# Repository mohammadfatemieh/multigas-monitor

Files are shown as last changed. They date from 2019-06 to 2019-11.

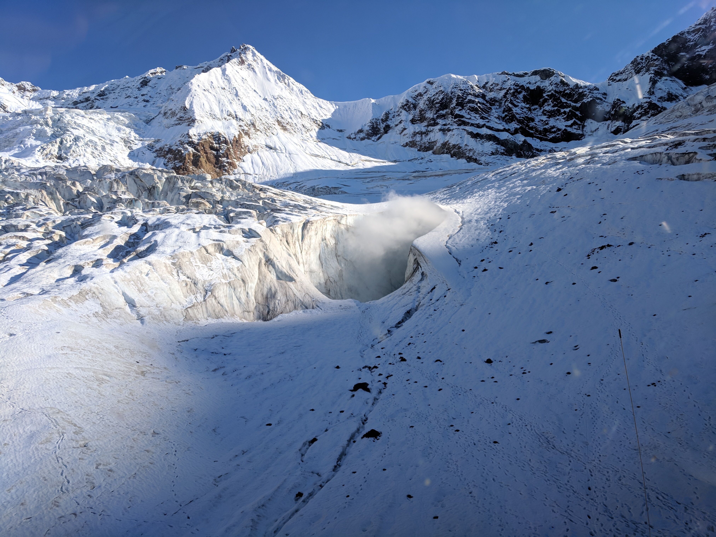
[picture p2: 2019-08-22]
Documents/FUMAROLE.jpeg

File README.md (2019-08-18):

# VAMoS MultiGas Monitor
Research instrument for monitoring gaseous concentrations.

## Overview
The VAMoS MultiGas Monitor is an improvement to the exisiting MGM used by SFU Volcanology. The current MGM cannot be used for more than
1-2 hours and must be manually controlled by an on-site researcher. VAMoS is a device that can be deployed for multi-week remote
monitoring in the glacial environment on Mt. Meager's Job Glacier.

## Features
* Onboard microprocessing using the ESP32WROOM-32U micrcontroller
* Inverted-F trace antenna for WiFi transmission at 2.4GHz
* 4-20mA signal processing for state-of-the-art Alphasense electrochemical and NDIR gas sensors
* Onboard BME280 temperature, humidity, and pressure sensor; XA1100 GPS module
* Connector for external DS18B20 temperature probe
* microSD card connector for data storage
* LED indicators to show system health and operation status

## Known Issues
* See document

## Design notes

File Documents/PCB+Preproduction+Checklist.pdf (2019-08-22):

# PCB Preproduction Checklist

ID | Item | Check

0.0 Schematic

0.1 | Boot strapping note added to MCU sheet? Triple-check default states due to internal vs. external pull-up/pull-down resistors.
0.2 | Boot strapping pins accessible via TPs?
0.3 | Debug pins broken out to SMD header?
0.4 | Test points on all unused pins?
0.5 | Small ceramic bypass cap on enable/reset lines?
0.6 | Noise-sensitive analog systems have separate power rail from low-noise LDO? Inside a grounded RF shield?
0.7 | All peripherals have TVS diodes as gatekeeper?
0.8 | All (UART, SPI, etc.) signals have 0R series resistors to make placeholder for ferrite bead?
0.9 | Check default internal state of IO pins (pull-up vs. pull-down) and add external resistors where necessary. Option to add both and DNP where necessary.

1.0 Footprints

1.1 | All components have 3D extrusion?
1.2 | Footprints double-checked?
1.3 | Footprints triple-checked?
1.4 | Detailed 3D CAD populated for all ICs, especially connectors? Check manufacturer website if not available through distributor.
1.4 | Connectors facing outwards?
1.5 | Pin 1 indicator present on silkscreen of all ICs? Polarity (e.g. diodes, LEDs, electrolytic caps) indicated?

2.0 Power Plane

2.1 | Islands for separate rails?

2.2 Island bridges ~20 mil width (check with trace width calculator)

3.0 Ground Plane

3.1 | Stitching vias?
3.2 | Direct connect polygons for GND vias?
3.3 | No net antennae on DRC? Add vias to planes that extend into stubs without enough stitching vias.

4.0 Vias

4.1 | Tented on top and bottom (except for thermal relief GND vias underneath large ICs)?
4.2 | 10-20mil ratio?

5.0 Miscellaneous

5.1 | Mounting holes in each corner, M3 (3mm dia) screws
5.2 | Board outline defined on Keep-Out or Mechanical 1 layer with curved edges
5.3 | Board outlines clearance set to 20-40mil
5.4 | Useful TP and connector labels on silkscreen? Specify polarity of power inputs, DC vs. AC, boot strapping TPs, status LEDs, power rails, and ground TPs.
5.5 | Light passives (e.g. 0402, 0603 or less) have even amount of copper pours on either side to ensure equal melt distribution?

6.0 Manufacturability

6.1 | Min. 3 fiducials per side to ensure manufacturing alignment?
6.2 | No acid traps (acute angle traces?)
6.3 | Latest PCB design rules (.RUL) imported as per manufacturer's specifications?
6.4 | Board thickness/stack-up is 1.6mm / 63mil (for four-layer) PCB?

7.0 RF

7.1 | Antenna trace length impedance matched?
7.2 | Ground vias around perimeter?
7.3 | External/shielding pins of connector (if applicable) grounded?

8.0 Power Supply

8.1 | Bypass caps close to IC, in order of lowest capacitance to highest?
8.2 | High-frequency traces thick (min. pad thickness, if possible use a plane)

8.3 | No traces underneath switching inductor?
8.4 | Via ampacity: 18-35mil in/out diameter via on power traces? Multiple for connecting large planes (use min. 3 vias or make larger). Check with trace width calculator, specifically for internal layers.

9.0 Bill of Materials (BOM)

9.1 | Only CT (Cut Tape) PNs used? (Digi-Reel costs extra $8-10)
9.2 | Checked twice?
9.3 | Checked thrice?

10.0 Post Production

10.1 | Export 3D STEP model of PCB for enclosure design team
10.2 | Zip release files and label with board house and order date
10.3 | Upload all project files to GitHub
10.4 | Order BOM. If sufficient amount of parts are cheaper through Mouser, Future, etc. and cart is large enough to get free shipping on all orders, then order through multiple distributors. Otherwise, order through DigiKey.

FINAL CHECK:

Is the PCB looking SEX? | HELL YEAH | NAH

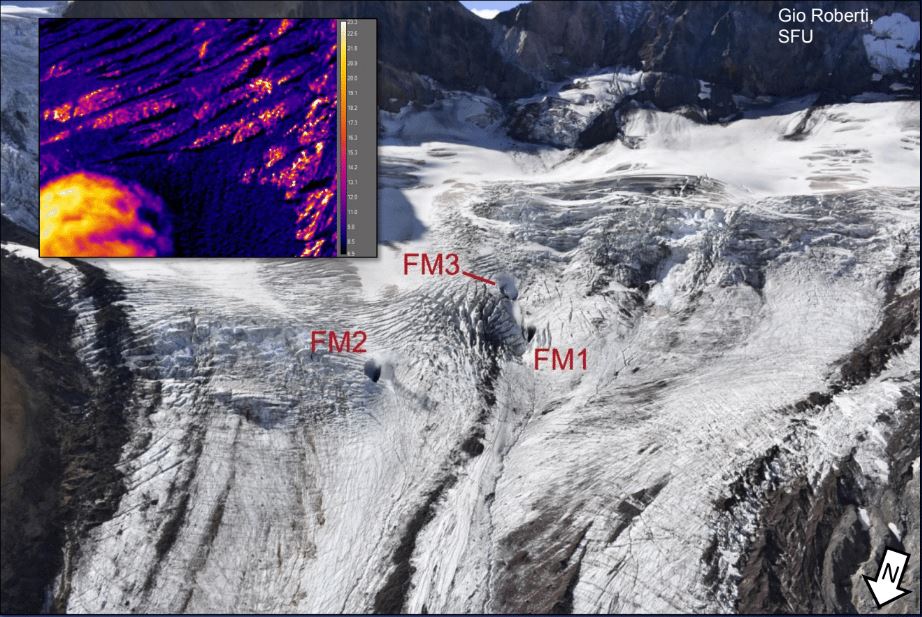
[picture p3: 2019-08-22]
Documents/fumaroles.JPG

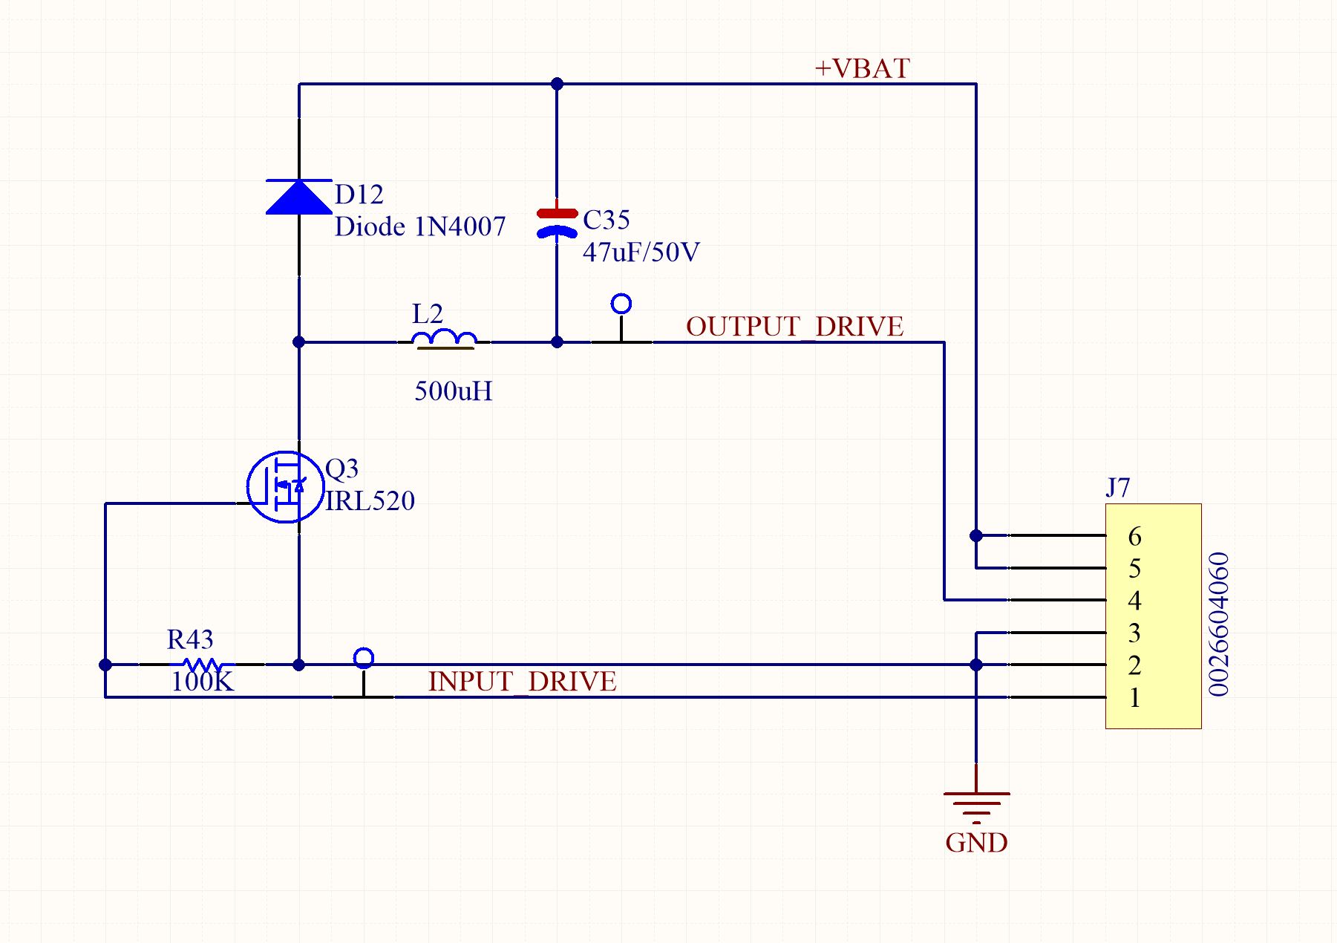
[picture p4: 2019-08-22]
Documents/pumpdrive.JPG

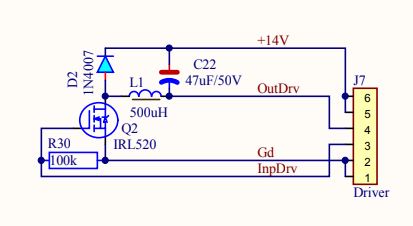
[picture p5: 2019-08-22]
Documents/Pump Driver.JPG

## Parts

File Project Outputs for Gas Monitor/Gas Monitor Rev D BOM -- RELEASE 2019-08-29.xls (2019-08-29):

Description | Designator | Footprint | Quantity | Manufacturer | Manufacturer Part Number | Supplier 1 | Supplier Part Number 1 | Value | VAMoS Rev D
Push Button Top | B200, B201 | PTS 815 | 2 | C&K Components | PTS815 SJG 250 SMTR LFS | Digi-Key | CKN12217-1-ND |  | BOM
 | C100, C101, C102, C103, C104, C105, C106, C107, C108, C109, C110, C111, C112, C113, C114, C115, C116, C117, C200, C202, C204, C205, C206, C208, C209, C306, C311, C318, C405, C406, C407, C501, C502, C503, C605, C608 | CAPC1005X06N | 36 | Samsung | CL05A104KA5NNNC | Digi-Key | 1276-1043-1-ND | 100nF | 2019-08-29
Capacitor | C201 | CAPC1005X06N | 1 | Samsung | CL05A106MP8NUB8 | Digi-Key | 1276-6830-1-ND | 10u
Cap,4.7uF,10V,20%,X5R,0402, Cap,4.7uF,16V,20%,X5R,0402 | C203, C207, C300, C302, C305, C307, C312, C313, C314, C317 | C1005[0402] | 10 | Samsung Electro-Mechanics | CL05A475MO5NUNC | Digi-Key | 1276-6836-1-ND | 4u7
 | C303, C304, C315, C321, C322, C603, C609, C610, C611 | CAPC2012X14N | 9 | Murata | GRM21BR61E226ME44K | Digi-Key | 490-14661-1-ND | 22u
 | C308, C319 | CAPC1005X06N | 2 | Samsung | CL05B153KO5NNNC | Digi-Key | 1276-1524-1-ND | 15n
Cap,3.3nF,50V,10%,X7R,0603 | C309 | C1608[0603] | 1 | Samsung | CL10B332KB8NNNC | Digi-Key | 1276-1758-1-ND | 3n3
 | C310, R227 | CAPC1005X06N, RESC1005X03N | 2 | N/A | N/A | N/A | N/A | DNP
 | C316, C320 | C3225[1210]_Tall | 2 | Murata | GRM32ER61A107ME20L | Digi-Key | 490-9969-1-ND | 100u
CAP 4.7uF 10V ±10% X5R 0603 | C400, C401, C402, C403, C404 | CAPC1005X06N | 5 | Samsung | CL05A105MP5NNNC | Digi-Key | 1276-1448-1-ND | 1u
CAP ALUM 47UF 20% 50V SMD | C500 | Panasonic S-V D8 | 1 | Panasonic | EEE-1HA470XAP | Digi-Key | PCE4622CT-ND
CAP 1µF 25V ±10% X7R 0603 | C600, C601, C602, C604, C606, C607 | C1608[0603] small | 6 | Samsung | CL10B105KA8NNNC | Digi-Key | 1276-1184-1-ND | 1u
5V TVS | D100, D101, D102, D103, D104, D105, D106, D107, D200, D209 | NXP PTVSxS1UR-Series (SOD123W) | 10 | Nexperia | PTVS5V0S1UR,115 | Digi-Key | 1727-5229-1-ND
TVS Diode | D201, D202, D203, D205, D206 | SODFL100X40-2N | 5 | ON Semiconductor | ESD7951ST5G | Digi-Key | ESD7951ST5GOSCT-ND
LED RGB Clear 624nm/526nm/469nm 2V/3.1V/3V PLCC-6 | D208 | VLMRGB6112 | 1 | Vishay Semiconductor Opto Division | VLMRGB6112-00-GS08 | Digi-Key | VLMRGB6112-00-GS08CT-ND
12V TVS | D300, D501, D502, D600, D601, D602 | NXP PTVSxS1UR-Series (SOD123W) | 6 | Nexperia | PTVS12VS1UR,115 | Digi-Key | 1727-5325-1-ND
LED Blue Diffused 0603 | D301 | LED_0603 | 1 | Rohm | SMLE12BC7TT86 | Digi-Key | 511-1589-1-ND
LED Green Diffused 0603 | D302, D303, D304, D305, D407, D606 | LED_0603 | 6 | Rohm | SML-D12M8WT86 | Digi-Key | 511-1578-1-ND
Diode Standard 600V 2A Surface Mount SMA | D306, D500, D603, D604, D605 | Diode SMA DIOM5226X240N | 5 | ON Semi | MURA260T3G | Digi-Key | MURA260T3GOSCT-ND
3.3V TVS | D400, D401, D402, D403, D404, D405 | NXP PTVSxS1UR-Series (SOD123W) | 6 | Nexperia | PTVS3V3S1UTR,115 | Digi-Key | 1727-1416-1-ND
300mA General Purpose | D406 | SOD-123FL_TVS | 1 | Diodes Incorporated | 1N4148W-7-F | Digi-Key | 1N4148W-FDICT-ND
120 Ohms @ 100MHz 1 Power Line Ferrite Bead 0603 (1608 Metric) 2.7A 35mOhm | FB500 | RESC1608X06N | 1 | Taiyo Yuden | BKP1608HS121-T | Digi-Key | 587-1923-1-ND
CONN HEADER VERT 2POS 2.54MM | J100, J101, J102, J103 | 22-23-2021 | 4 | Molex | 22-23-2021 | Digi-Key | WM4200-ND
Connector Header Through Hole 4 position 0.100" (2.54mm) | J104, J105, J106, J107, J401 | 22-23-2041 | 5 | Molex | 22232041 | Digi-Key | WM4202-ND
CONN HEADER VERT 2POS 2.54MM | J200 | HDR_1x2_0.100" | 1 | Sullins | PRPC002SAAN-RC | Digi-Key | S1011EC-02-ND
 | J201 | SD-47219-001 | 1 | Molex | 472192001 | Digi-Key | WM6698CT-ND
Connector Header Through Hole 3 position 0.100" (2.54mm) | J202, J400, J500 | 22-23-2031 | 3 | Molex | 22232031 | Digi-Key | WM4201-ND
 | J203 | UJ2-MIBH2-4-SMT | 1 | CUI | UJ2-MIBH2-4-SMT-TR | Digi-Key | 102-4007-1-ND
5.08mm Spring Cage, Tension Clamp, Pheonix Contact, 2pos, THD | J300, J600, J601, J602 | 5.08MM 2POS TERMBLOCK | 4 | Phoenix Contact | 1790283 | Digi-Key | 277-6722-ND
DigiKey # 36-2997-ND | J402 | 2997 11.6MM COIN CELL | 1 | Keystone Electronics | 2997 | Digi-Key | 36-2997-ND
CONUFL001-SMD-T | J403 | CONUFL001-SMD-T | 1 | Linx Technologies | CONUFL001-SMD-T | Digi-Key | CONUFL001-SMD-TCT-ND
Ferrite,SMD,3A,30Ohm,0805 | L300, L301, L400 | L2012[0805] | 3 | Bourns Inc. | MH2029-300Y | Digi-Key | MH2029-300YCT-ND
2 Line Common Mode Choke Surface Mount 60 Ohms @ 100MHz 15A DCR 0.75mOhm | L302, L600, L601, L602 | CM3421Y600R-10 | 4 | Laird | CM3421Y600R-10 | Digi-Key | 240-2501-1-ND
Fixed Inductor,SMD,33nH,550mA,132mOhmDCR,2.5GHz,0603 | L401 | L1608[0603] | 1 | Murata | LQW18AN33NJ10D | Digi-Key | 490-6885-1-ND | 33n
470µH Shielded Wirewound Inductor 1.4A 560mOhm Max Nonstandard | L500 | WE-PD 1210 | 1 | Wurth Electronics | 7447709471 | Digi-Key | 732-1699-1-ND | 470u
General Purpose Transistor, NPN Silicon, 3-Pin SOT-23, Tape and Reel | Q200, Q201 | ONSC-SOT-23-3-318-08_V | 2 | Comchip Technology | SS8050-G | Digi-Key | 641-1790-1-ND
MOSFET N-CH 100V 28A D2PAK | Q500 | D2PAK | 1 | Vishay Siliconix | IRL540SPBF | Digi-Key | IRL540SPBF-ND
RES 1K Ohm ±5%, 0.25W,1/4W 0603 | R100, R105, R106, R107, R112, R114, R116, R118, R215 | RESC1005X03N | 9 | Panasonic | ERJ-2RKF1001X | Digi-Key | P1.00KLCT-ND | 1k
Res,SMD,4R99,1/4W,5% | R101, R102, R103, R104, R113, R115, R117, R119 | RESC1005X03N | 8 | Stackpole | RMCF0402FT4R99 | Digi-Key | RMCF0402FT4R99CT-ND | 4R99
Res,SMD,22k,0603,5%,1/4W | R108, R109, R110, R111, R120, R121, R122, R123 | RESC1005X03N | 8 | Panasonic | ERJ-2RKF2202X | Digi-Key | P22.0KLDKR-ND | 22k
 | R200, R201, R202, R203, R204, R205, R206, R209, R210, R212, R221, R222, R223, R233 | RESC1005X03N | 14 | Panasonic | ERJ-2GE0R00X | Digi-Key | P0.0JCT-ND | 0R
Res,SMD,1/10W,3K16,0603,1% | R216 | RESC1005X03N | 1 | Stackpole Electronics | RMCF0603FT3K16 | Digi-Key | RMCF0603FT3K16CT-ND | 3k16
Res,SMD,4K53,1/10W,1%,0603 | R217 | RESC1005X03N | 1 | Yageo | RC0603FR-074K53L | Digi-Key | 311-4.53KHRCT-ND | 4k53
RES 10k Ohm, [NoValue], RES 1K Ohm ±5%, 0.25W,1/4W 0603 | R220, R228, R229, R230, R300, R304, R400, R404, R405, R406, R409 | RESC1005X03N | 11 | Panasonic | ERJ-2RKF1002X | Digi-Key | P10.0KLCT-ND | 10k
Res,SMD,22k,0603,5%,1/4W | R224 | R1005[0402] | 1 | Panasonic | ERJ-2RKF2212X | Digi-Key | P22.1KLCT-ND | 22k1
Res,SMD,22k,0603,5%,1/4W | R225 | R1005[0402] | 1 | Panasonic | ERJ-2RKF4752X | Digi-Key | P47.5KLCT-ND | 47k5
 | R226, R407, R408 | R1005[0402] | 3 | Panasonic | ERJ-2RKF2001X | Digi-Key | P2.00KLDKR-ND | 2k
 | R231 | RESC1005X03N | 1 | Panasonic | ERJ-2RKF6981X | Digi-Key | P6.98KLCT-ND | 6k98
 | R232 | RESC1005X03N | 1 | Panasonic | ERJ-2RKF2101X | Digi-Key | P2.10KLCT-ND | 2k1
Res,SMD,0603,1/10W,100K,1% | R301 | RESC1005X03N | 1 | Panasonic | ERJ-2RKF1003X | Digi-Key | P100KLCT-ND | 100k
RES 1K Ohm ±5%, 0.25W,1/4W 0603 | R302, R305, R602 | R1608[0603] small | 3 | Yageo | RC0603FR-071K2L | Digi-Key | 311-1.20KHRCT-ND
RES SMD 71.5K OHM 1% 1/10W 0603 | R303 | RESC1005X03N | 1 | Panasonic Electronic Components | ERJ-2RKF7152X | Digi-Key | P71.5KLCT-ND
RES 1K Ohm ±5%, 0.25W,1/4W 0603 | R306, R307 | R1608[0603] small | 2 | Rohm | RC0603FR-07560RL | Digi-Key | 311-560HRCT-ND
RES 1K Ohm ±5%, 0.25W,1/4W 0603 | R308, R401 | R1608[0603] small | 2 | Rohm | RC0603FR-07330RL | Digi-Key | 311-330HRCT-ND | 330R
RES 1K Ohm ±5%, 0.25W,1/4W 0603 | R402, R403 | RESC1005X03N | 2 | Panasonic | ERJ-2RKF4700X | Digi-Key | P470LCT-ND | 470R
 | R500 | RESC1608X06N | 1 | Panasonic | ERJ-3GEY0R00V | Digi-Key | P0.0GCT-ND | 0R
 | R501 | RESC1608X06N | 1 | Panasonic | ERJ-3GEYJ104V | Digi-Key | P100KGCT-ND | 100k
 | R600 | RESC1608X06N | 1 | Panasonic | ERA-3AEB5362V | Digi-Key | P53.6KDBCT-ND | 53k6
 | R601 | RESC1608X06N | 1 | Panasonic | ERA-3AEB6981V | Digi-Key | P6.98KDBCT-ND | 6k98
Quad opamplifiers | U100, U101 | SOIC-14 | 2 | Texas Instruments | LMH6644MAX/NOPB | Digi-Key | 296-35336-1-ND
Microcontroller WIFI Module 32Mbits SPI Flash | U200 | ESP32-WROOM-32U | 1 | Espressif Systems | ESP32-WROOM-32U | Digi-Key | 1904-1026-1-ND
USB to UART converter | U201 | QFN50P500X500X80_HS-29N | 1 | Silicon Labs | CP2102N-A01-GQFN28R | Digi-Key | 336-4738-1-ND
USB ESD Solution with Power Clamp, 4 Channels, -40 to +85 degC, 6-pin SON (DRY), Green (RoHS & no Sb/Br) | U202 | DRY0006A | 1 | Texas Instruments | TPD4S012DRYR | Digi-Key | 296-24244-1-ND
1A 3.3V LDO | U300 | SOT230P700X165-4N | 1 | Diodes Incorporated | ZLDO1117G50TA | Digi-Key | ZLDO1117G50DICT-ND
High Side Load Switch | U301 | SOT23 | 1 | Texas Instruments | TPS22810DBVR | Digi-Key | 296-45297-1-ND
DC-DC: 0.9-6V 2A output, 3-17V input. Non-isolated. | U302 | SIL0008D | 1 | Texas Instruments | TPS82140SILT | Digi-Key | 296-47089-1-ND
1A 3.3V LDO | U303 | SOT230P700X165-4N | 1 | Diodes Incorporated | ZLDO1117QG33TA | Digi-Key | ZLDO1117QG33TADICT-ND
GPS Module | U400 | XA1100 | 1 | Sierra Wireless | XA1100_1103872 | Digi-Key | 1645-1094-1-ND
SENSOR Humidity Temperature 0 ~ 100% RH I²C SPI ±3% 1s 8-Pin LGA | U401 | BME280 | 1 | Bosch | BME280 | Digi-Key | 828-1063-1-ND
Linear Voltage Regulator IC Positive Adjustable 1 Output 3A D2PAK-5 | U600 | D2PAK-5 | 1 | ON Semiconductor | NCP57302DSADJR4G | Digi-Key | NCP57302DSADJR4GOSCT-ND
Coin cell battery 11.6mm Silver Oxide |  |  | 2 | Energizer Battery Company | 357-303VZ | Digi-Key | N102-ND
Molex 22-23 2pin housing |  |  | 10 | Molex | 22-01-3027 | Digi-Key | WM2000-ND
Molex 22-23 3pin housing |  |  | 12 | Molex | 22-01-3037 | Digi-Key | WM2001-ND
Molex 22-23 4pin housing |  |  | 10 | Molex | 22013047 | Digi-Key | WM2002-ND
Molex KK crimp tool set |  |  | 1 | Molex | 76650-0009 | Digi-Key | WM9983-ND
TE AMP FASTON connector |  |  | 10 | TE Connectivity | 444334-3 | Digi-Key | A117966CT-ND
TE AMP FASTON sleeve |  |  | 10 | TE Connectivity | 170823-6 | Digi-Key | A106979-ND

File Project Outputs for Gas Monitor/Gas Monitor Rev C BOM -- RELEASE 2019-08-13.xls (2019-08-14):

Description | Designator | Footprint | Quantity | Supplier 1 | Supplier Part Number 1 | Manufacturer | Manufacturer Part Number
Push Button Top | B200, B201 | PTS 815 | 2 | Digi-Key | CKN12217-1-ND | C&K Components | PTS815 SJG 250 SMTR LFS
 | C100, C101, C102, C103, C104, C105, C106, C107, C200, C202, C204, C206, C208, C209, C306, C311, C318, C405, C406, C407, C408, C409 | CAPC1005X06N | 22 | Digi-Key | 1276-1043-1-ND | Samsung | CL05A104KA5NNNC
Capacitor | C201 | CAPC1005X06N | 1 | Digi-Key | 1276-6830-1-ND | Samsung | CL05A106MP8NUB8
Cap,4.7uF,10V,20%,X5R,0402, Cap,4.7uF,16V,20%,X5R,0402 | C203, C207, C300, C302, C305, C307, C312, C313, C314, C317 | C1005[0402] | 10 | Digi-Key | 1276-6836-1-ND | Samsung Electro-Mechanics | CL05A475MO5NUNC
CAP 1µF 25V ±10% X7R 0603 | C301 | C1608[0603] small | 1 | Digi-Key | 1276-1184-1-ND | Samsung | CL10B105KA8NNNC
22uF 50V Hybrid Polymer Capacitor | C303 | Radial Can F61 6.6x6.6 | 1 | Digikey | 565-4188-6-ND | United Chemi-Con | HHXB500ARA220MF61G
CAP 22µF 16V ±20% X5R 0805 | C304 | C2012[0805] | 1 | Digi-Key | 1276-6780-1-ND | Samsung Electro-Mechanics | CL21A226MOCLRNC
 | C308, C319 | CAPC1005X06N | 2 | Digi-Key | 1276-1524-1-ND | Samsung | CL05B153KO5NNNC
Cap,3.3nF,50V,10%,X7R,0603 | C309 | C1608[0603] | 1 | Digi-Key | 1276-1758-1-ND | Samsung | CL10B332KB8NNNC
 | C315 | Radial Can Size G | 1 | Digikey | P15442CT-ND | Panasonic | EEH-ZA1H101P
 | C316 | C3225[1210]_Tall | 1 | Digi-Key | 490-9969-1-ND | Murata | GRM32ER61A107ME20L
CAP 4.7uF 10V ±10% X5R 0603 | C400, C401, C402, C403, C404 | CAPC1005X06N | 5 | Digi-Key | 1276-1448-1-ND | Samsung | CL05A105MP5NNNC
5V TVS | D100, D101, D102, D103, D104, D105, D106, D107 | NXP PTVSxS1UR-Series (SOD123W) | 8 | Digi-Key | 1727-5229-1-ND | Nexperia | PTVS5V0S1UR,115
3.3V TVS | D200, D201, D400, D401, D402, D403, D404, D405, D409, D410 | NXP PTVSxS1UR-Series (SOD123W) | 10 | Digi-Key | 1727-1416-1-ND | Nexperia | PTVS3V3S1UTR,115
TVS Diode | D202, D203, D204, D205, D206, D207 | SODFL100X40-2N | 6 | Digi-Key | ESD7951ST5GOSCT-ND | ON Semiconductor | ESD7951ST5G
LED RGB Clear 624nm/526nm/469nm 2V/3.1V/3V PLCC-6 | D208 | VLMRGB6112 | 1 | Digi-Key | VLMRGB6112-00-GS08CT-ND | Vishay Semiconductor Opto Division | VLMRGB6112-00-GS08
12V TVS | D300 | NXP PTVSxS1UR-Series (SOD123W) | 1 | Digi-Key | 1727-5325-1-ND | Nexperia | PTVS12VS1UR,115
LED Green Diffused 0603 | D301, D302, D303, D304, D305, D407 | LED_0603 | 6 | Digi-Key | 511-1578-1-ND | Rohm | SML-D12M8WT86
300mA General Purpose | D406 | SOD-123FL_TVS | 1 | Digi-Key | 1N4148W-FDICT-ND | Diodes Incorporated | 1N4148W-7-F
Connector Phoenix 10 pin | J100 | 6410/10pin | 1 | Digi-Key | WM4308-ND | Molex | 22053101
Connector 2 pin | J200 | 6410/2pin | 1 | Digi-Key | WM19468-ND | Molex | 22232023
 | J201 | SD-47219-001 | 1 | Digi-Key | WM6698CT-ND | Molex | 472192001
 | J202 | 502584-0370 | 1 | Digi-Key | WM14461CT-ND | Molex | 5025840370
 | J203 | UJ2-MIBH2-4-SMT | 1 | Digi-Key | 102-4007-1-ND | CUI | UJ2-MIBH2-4-SMT-TR
5.08mm Spring Cage, Tension Clamp, Pheonix Contact, 2pos, THD | J300 | 5.08MM 2POS TERMBLOCK | 1 | Digi-Key | 277-6722-ND | Phoenix Contact | 1790283
3POS,THD,TENSION CLAMP,PHOENIX CONTACT | J400 | 3POS PHOENIX | 1 | Digi-Key | 277-1623-ND | Phoenix Contact | 1985205
 | J401 | 502584-0470 | 1 | Digi-Key | WM10615CT-ND | Molex | 502584-0470
DigiKey # 36-2997-ND | J402 | 2997 11.6MM COIN CELL | 1 | Digi-Key | 36-2997-ND | Keystone Electronics | 2997
CONUFL001-SMD-T | J403 | CONUFL001-SMD-T | 1 | Digi-Key | CONUFL001-SMD-TCT-ND | Linx Technologies | CONUFL001-SMD-T
0.100" Female Header | J404 | 0.100" 9PIN | 1 | Digi-Key | S7042-ND | Sullins | PPPC091LFBN-RC
Ferrite,SMD,3A,30Ohm,0805 | L300, L301, L400 | L2012[0805] | 3 | Digi-Key | MH2029-300YCT-ND | Bourns Inc. | MH2029-300Y
Fixed Inductor,SMD,33nH,550mA,132mOhmDCR,2.5GHz,0603 | L401 | L1608[0603] | 1 | Digi-Key | 490-6885-1-ND | Murata | LQW18AN33NJ10D
General Purpose Transistor, NPN Silicon, 3-Pin SOT-23, Tape and Reel | Q200, Q201 | ONSC-SOT-23-3-318-08_V | 2 | Digi-Key | 641-1790-1-ND | Comchip Technology | SS8050-G
RES 1K Ohm ±5%, 0.25W,1/4W 0603 | R100, R105, R106, R107, R112, R114, R116, R118 | RESC1005X03N | 8 | Digi-Key | P1.00KLCT-ND | Panasonic | ERJ-2RKF1001X
Res,SMD,4R99,1/4W,5% | R101, R102, R103, R104, R113, R115, R117, R119 | RESC1005X03N | 8 | Digi-Key | RMCF0402FT4R99CT-ND | Stackpole | RMCF0402FT4R99
Res,SMD,22k,0603,5%,1/4W | R108, R109, R110, R111, R120, R121, R122, R123 | RESC1005X03N | 8 | Digi-Key | P22.0KLDKR-ND | Panasonic | ERJ-2RKF2202X
 | R200, R201, R202, R203, R204, R205, R206, R207, R208, R209, R210, R211, R221, R222, R223 | RESC1005X03N | 15 | Digi-Key | P0.0JCT-ND | Panasonic | ERJ-2GE0R00X
RES 1K Ohm ±5%, 0.25W,1/4W 0603 | R215 | R1608[0603] small | 1 | Digi-Key | RHM1.0KDCT-ND | Rohm | ESR03EZPJ102
Res,SMD,1/10W,3K16,0603,1% | R216 | R1608[0603] small | 1 | Digi-Key | RMCF0603FT3K16CT-ND | Stackpole Electronics | RMCF0603FT3K16
Res,SMD,4K53,1/10W,1%,0603 | R217 | R1608[0603] small | 1 | Digi-Key | 311-4.53KHRCT-ND | Yageo | RC0603FR-074K53L
Res,SMD,22k,0603,5%,1/4W | R224 | R1005[0402] | 1 | Digi-Key | P22.1KLCT-ND | Panasonic | ERJ-2RKF2212X
Res,SMD,22k,0603,5%,1/4W | R225 | R1005[0402] | 1 | Digi-Key | P47.5KLCT-ND | Panasonic | ERJ-2RKF4752X
 | R226, R407, R408 | R1005[0402] | 3 | Digi-Key | P2.00KLDKR-ND | Panasonic | ERJ-2RKF2001X
 | R228, R229, R230, R300, R400 | RESC1005X03N | 5 | Digi-Key | P10.0KLCT-ND | Panasonic | ERJ-2RKF1002X
Res,SMD,0603,1/10W,100K,1% | R301 | RESC1005X03N | 1 | Digi-Key | P100KLCT-ND | Panasonic Electronic Components | ERJ-2RKF1003X
RES 1K Ohm ±5%, 0.25W,1/4W 0603 | R302, R305 | R1608[0603] small | 2 | Digi-Key | 311-1.20KHRCT-ND | Yageo | RC0603FR-071K2L
RES SMD 71.5K OHM 1% 1/10W 0603 | R303 | RESC1005X03N | 1 | Digi-Key | P71.5KLCT-ND | Panasonic Electronic Components | ERJ-2RKF7152X
RES 1K Ohm ±5%, 0.25W,1/4W 0603 | R304 | RESC1005X03N | 1 | Digi-Key | P10.0KLCT-ND | Panasonic | ERJ-2RKF1002X
RES 1K Ohm ±5%, 0.25W,1/4W 0603 | R306, R307 | R1608[0603] small | 2 | Digi-Key | 311-560HRCT-ND | Rohm | RC0603FR-07560RL
RES 1K Ohm ±5%, 0.25W,1/4W 0603 | R308, R401 | R1608[0603] small | 2 | Digi-Key | 311-330HRCT-ND | Rohm | RC0603FR-07330RL
RES 1K Ohm ±5%, 0.25W,1/4W 0603 | R402, R403 | RESC1005X03N | 2 | Digi-Key | P470LCT-ND | Panasonic | ERJ-2RKF4700X
RES 1K Ohm ±5%, 0.25W,1/4W 0603 | R404, R405, R406, R409 | RESC1005X03N | 4 | Digi-Key | P10.0KLDKR-ND | Panasonic | ERJ-2RKF1002X
Quad opamplifiers | U100, U101 | SOIC-14 | 2 | Digi-Key | LMC660CMX/NOPBCT-ND | Texas Instruments | LMC660CMX/NOPB
Espressif System, 2.7 to 3.6 V, -40 to 85 degC, 38-Pin SMD | U200 | OLMX-ESP-WROOM-32 | 1 | Digi-Key | 1904-1026-1-ND | Espressif Systems | ESP32-WROOM-32U
USB to UART converter | U201 | QFN50P500X500X80_HS-29N | 1 | Digi-Key | 336-4738-1-ND | Silicon Labs | CP2102N-A01-GQFN28R
USB ESD Solution with Power Clamp, 4 Channels, -40 to +85 degC, 6-pin SON (DRY), Green (RoHS & no Sb/Br) | U202 | DRY0006A | 1 | Digi-Key | 296-24244-1-ND | Texas Instruments | TPD4S012DRYR
1A 3.3V LDO | U300 | SOT230P700X165-4N | 1 | Digi-Key | ZLDO1117G50DICT-ND | Diodes Incorporated | ZLDO1117G50TA
High Side Load Switch | U301 | SOT23 | 1 | Digi-Key | 296-45297-1-ND | Texas Instruments | TPS22810DBVR
DC-DC: 0.9-6V 2A output, 3-17V input. Non-isolated. | U302 | SIL0008D | 1 | Digi-Key | 296-47089-1-ND | Texas Instruments | TPS82140SILT
1A 3.3V LDO | U303 | SOT230P700X165-4N | 1 | Digi-Key | ZLDO1117QG33TADICT-ND | Diodes Incorporated | ZLDO1117QG33TA
GPS Module | U400 | XA1100 | 1 | Digi-Key | 1645-1094-1-ND | Sierra Wireless | XA1100_1103872
SENSOR Humidity Temperature 0 ~ 100% RH I²C SPI ±3% 1s 8-Pin LGA | U401 | BME280 | 1 | Digi-Key | 828-1063-1-ND | Bosch | BME280
0.100" Female Header | U402 | 0.100" 7PIN | 1 | Digi-Key | S7040-ND | Molex | PPPC071LFBN-RC

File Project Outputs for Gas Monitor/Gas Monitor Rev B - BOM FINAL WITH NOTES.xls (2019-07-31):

Description | Designator | Footprint | Quantity | Multiplier (# boards) | Total | Supplier Part Number 1 | Supplier 1 | Manufacturer | Manufacturer Part Number
SENSOR Humidity Temperature 0 ~ 100% RH I²C SPI ±3% 1s 8-Pin LGA | U11 | BME280 | 1 | 2 | 2 | 828-1063-1-ND | Digi-Key | Bosch | BME280
Ferrite,SMD,3A,30Ohm,0805 | L1, L2, L4 | L2012[0805] | 3 | 2 | 6 | MH2029-300YCT-ND | Digi-Key | Bourns Inc. | MH2029-300Y
Push Button Top | B1, B2 | PTS 815 | 2 | 2 | 4 | CKN12217-1-ND | Digi-Key | C&K Components | PTS815 SJG 250 SMTR LFS
 | U7 | UJ2-MIBH2-4-SMT | 1 | 2 | 2 | 102-4007-1-ND | Digi-Key | CUI | UJ2-MIBH2-4-SMT-TR
QSPI 128M Flash Memory | U12 | SOIC127P1030X265-16N | 1 | 2 | 2 | 428-4172-ND | Digi-Key | Cypress Semiconductor Corp | S25FL128SDPMFIG10
1A 3.3V LDO | U4 | SOT230P700X165-4N | 1 | 2 | 2 | ZLDO1117G50DICT-ND | Digi-Key | Diodes Incorporated | ZLDO1117G50TA
1A 3.3V LDO | U6 | SOT230P700X165-4N | 1 | 2 | 2 | ZLDO1117QG33TADICT-ND | Digi-Key | Diodes Incorporated | ZLDO1117QG33TA
300mA General Purpose, [NoValue] | D9, D10 | SOD-123FL_TVS | 2 | 2 | 4 | 1N4148W-FDICT-ND | Digi-Key | Diodes Incorporated | 1N4148W-7-F
32.768 kHz Crystal | Y1 | MC-146 | 1 | 2 | 2 | SER2416CT-ND | Digi-Key | EPSON | MC-146 32.768KA-AC3:ROHS
40MHz Crystal Oscillator | Y2 | FA-20H | 1 | 2 | 2 | SER4045CT-ND | Digi-Key | EPSON | FA-20H 40.0000MF10Z-K3
Microcontroller | U3 | QFN40P600X600X90_HS-49N | 1 | 2 | 2 | 1904-1004-1-ND | Digi-Key | Espressif Systems | ESP32-D0WDQ6
USB-UART Interface | U9 | SOP64P1030X175-20N | 1 | 2 | 2 | 768-1129-1-ND | Digi-Key | FTDI | FT231XS-R
Cap,5.6pF,200V,C0G/NP0,RF,0603 | C46 | C1608[0603] | 1 | 2 | 2 | 399-7944-1-ND | Digi-Key | KEMET | C0603C569C5GACTU
Ind,2.7nH,300mA,100mOhm DCR,13@100MHz,0603 | L3 | L1608[0603] | 1 | 2 | 2 | 399-9570-1-ND | Digi-Key | KEMET | L0603C2N7SRMST
DigiKey # 36-2997-ND | J6 | 2997 11.6mm COIN CELL | 1 | 2 | 2 | 36-2997-ND | Digi-Key | Keystone Electronics | 2997
MI0805K400R-10 | FB1 | MI0805K400R-10 | 1 | 2 | 2 | 240-2389-1-ND | Digi-Key | Laird | MI0805K400R-10
CONUFL001-SMD-T | J7 | CONUFL001-SMD-T | 1 | 2 | 2 | CONUFL001-SMD-TCT-ND | Digi-Key | Linx Technologies | CONUFL001-SMD-T
 | J9 | SD-47219-001 | 1 | 2 | 2 | WM6698CT-ND | Digi-Key | Molex | 472192001
 | J10 | TE_5-1814400-1 Upright | 1 | 2 | 2 | WM5544-ND | Digi-Key | Molex | 733910070
Connector 2 pin | J2 | 6410/2pin | 1 | 2 | 2 | WM19468-ND | Digi-Key | Molex | 22232023
Connector Phoenix 10 pin | J1 | 6410/10pin | 1 | 2 | 2 | WM4308-ND | Digi-Key | Molex | 22053101
 | C28 | C3225[1210]_Tall | 1 | 2 | 2 | 490-9969-1-ND | Digi-Key | Murata | GRM32ER61A107ME20L
Fixed Inductor,SMD,33nH,550mA,132mOhmDCR,2.5GHz,0603 | L5 | L1608[0603] | 1 | 2 | 2 | 490-6885-1-ND | Digi-Key | Murata | LQW18AN33NJ10D
Cap,2.4pF,100V,C0G/NP0,RF,0603 | C44 | C1608[0603] | 1 | 2 | 2 | 490-6093-1-ND | Digi-Key | Murata Electronics North America | GQM1885C2A2R4BB01D
 | J5 | Solder Small 4 Pos | 1 | 2 | 2 | N/A | N/A | N/A | N/A
3.3V TVS | D2, D26, D27, D28, D29, D30, D31, D32, D33, D35 | NXP PTVSxS1UR-Series (SOD123W) | 10 | 2 | 20 | 1727-1416-1-ND | Digi-Key | Nexperia | PTVS3V3S1UTR,115
5V TVS | D17, D18, D19, D20, D21, D22, D23, D24, D25 | NXP PTVSxS1UR-Series (SOD123W) | 9 | 2 | 18 | 1727-5229-1-ND | Digi-Key | Nexperia | PTVS5V0S1UR,115
12V TVS | D34 | NXP PTVSxS1UR-Series (SOD123W) | 1 | 2 | 2 | 1727-5325-1-ND | Digi-Key | Nexperia | PTVS12VS1UR,115
Dual NPN Transistors | U8 | SOT65P210X110-6N | 1 | 2 | 2 | MBT3904DW1T1GOSCT-ND | Digi-Key | ON Semiconductor | MBT3904DW1T1G
TVS Diode | D7, D8, D11, D12, D13, D14, D15, D16 | SODFL100X40-2N | 8 | 2 | 16 | ESD7951ST5GOSCT-ND | Digi-Key | ON Semiconductor | ESD7951ST5G
 | C27 | Radial Can Size G | 1 | 2 | 2 | P15442CT-ND | Digikey | Panasonic | EEH-ZA1H101P
 | R50, R51 | R1005[0402] | 2 | 2 | 4 | P2.00KLDKR-ND | Digi-Key | Panasonic | ERJ-2RKF2001X
RES 1K Ohm ±5%, 0.25W,1/4W 0603 | R1, R3, R5, R7, R13, R15, R17, R19, R39, R40, R45, R46, R47 | RESC1005X03N | 13 | 2 | 26 | P1.00KLCT-ND | Digi-Key | Panasonic | ERJ-2RKF1001X
RES 1K Ohm ±5%, 0.25W,1/4W 0603 | R38, R56, R57, R58, R59, R60, R61 | RESC1005X03N | 7 | 2 | 14 | P10.0KLCT-ND | Digi-Key | Panasonic | ERJ-2RKF1002X
RES 1K Ohm ±5%, 0.25W,1/4W 0603 | R41, R42 | RESC1005X03N | 2 | 2 | 4 | P27JCT-ND | Digi-Key | Panasonic | ERJ-2GEJ270X
RES 1K Ohm ±5%, 0.25W,1/4W 0603 | R43, R44, R48, R53, R54, R55 | RESC1005X03N | 6 | 2 | 12 | P10.0KLDKR-ND | Digi-Key | Panasonic | ERJ-2RKF1002X | remove this and order more P10.0KLCT-ND which is the cut tape version
RES 1K Ohm ±5%, 0.25W,1/4W 0603 | R49, R52 | RESC1005X03N | 2 | 2 | 4 | P470LCT-ND | Digi-Key | Panasonic | ERJ-2RKF4700X
RES SMD 71.5K OHM 1% 1/10W 0603 | R37 | RESC1005X03N | 1 | 2 | 2 | 311-71.5KHRCT-ND | Digi-Key | Panasonic | ERJ-2RKF7151X | changed to P71.5KLCT-ND ERJ-2RKF7152X Panasonic Electronic Components
Res,SMD,22k,0603,5%,1/4W | R9, R10, R11, R12, R21, R22, R23, R24 | RESC1005X03N | 8 | 2 | 16 | P22.0KLDKR-ND | Digi-Key | Panasonic | ERJ-2RKF2202X | replace with P22.0KLCT-ND, cut tape version
Resistor | R25 | R1005[0402] | 1 | 2 | 2 | P20KJDKR-ND | Digi-Key | Panasonic | ERJ-2GEJ203X
Resistor | R26 | RESC1005X03N | 1 | 2 | 2 | P499LCT-ND | Digi-Key | Panasonic | ERJ-2RKF4990X
Resistor | R31 | RESC1005X03N | 1 | 2 | 2 | P0.0JCT-ND | Digi-Key | Panasonic | ERJ-2GE0R00X
Res,SMD,0603,1/10W,100K,1% | R36 | RESC1005X03N | 1 | 2 | 2 | P100KLCT-ND | Digi-Key | Panasonic Electronic Components | ERJ-2RKF1003X
3POS,THD,TENSION CLAMP,PHOENIX CONTACT | J4 | 3POS PHOENIX | 1 | 2 | 2 | 277-1623-ND | Digi-Key | Phoenix Contact | 1985205
5.08mm Spring Cage, Tension Clamp, Pheonix Contact, 2pos, THD | J3 | 5.08mm 2pos TermBlock | 1 | 2 | 2 | 277-6722-ND | Digi-Key | Phoenix Contact | 1790283
LED Green Diffused 0603 | D3, D4, D5, D6 | LED_0603 | 4 | 2 | 8 | 511-1578-1-ND | Digi-Key | Rohm | SML-D12M8WT86
RES 1K Ohm ±5%, 0.25W,1/4W 0603 | R27 | R1608[0603] small | 1 | 2 | 2 | RHM1.0KDCT-ND | Digi-Key | Rohm | ESR03EZPJ102
RES 1K Ohm ±5%, 0.25W,1/4W 0603 | R33, R34 | R1608[0603] small | 2 | 2 | 4 | 311-560HRCT-ND | Digi-Key | Rohm | RC0603FR-07560RL
RES 1K Ohm ±5%, 0.25W,1/4W 0603 | R35 | R1608[0603] small | 1 | 2 | 2 | 311-330HRCT-ND | Digi-Key | Rohm | RC0603FR-07330RL
 | C1, C2, C3, C4, C5, C6, C7, C8, C21, C30, C33, C39, C41, C42, C43, C45, C47, C48, C49, C50, C53, C54, C56, C57, C58, C59, C60 | CAPC1005X06N | 27 | 2 | 54 | 1276-1043-1-ND | Digi-Key | Samsung | CL05A104KA5NNNC
 | C23, C31 | CAPC1005X06N | 2 | 2 | 4 | 1276-1524-1-ND | Digi-Key | Samsung | CL05B153KO5NNNC
CAP 1µF 25V ±10% X7R 0603 | C55 | C1608[0603] small | 1 | 2 | 2 | 1276-1184-1-ND | Digi-Key | Samsung | CL10B105KA8NNNC
CAP 4.7uF 10V ±10% X5R 0603 | C37, C38, C40, C51, C52 | CAPC1005X06N | 5 | 2 | 10 | 1276-1448-1-ND | Digi-Key | Samsung | CL05A105MP5NNNC
Cap,3.3nF,50V,10%,X7R,0603 | C24 | C1608[0603] | 1 | 2 | 2 | 1276-1758-1-ND | Digi-Key | Samsung | CL10B332KB8NNNC
CAP 22µF 16V ±20% X5R 0805 | C20 | C2012[0805] | 1 | 2 | 2 | 1276-6780-1-ND | Digi-Key | Samsung Electro-Mechanics | CL21A226MOCLRNC
Cap,4.7uF,16V,20%,X5R,0402, Cap,4.7uF,10V,20%,X5R,0402 | C17, C18, C22, C25, C26, C29, C32 | C1005[0402] | 7 | 2 | 14 | 1276-6836-1-ND | Digi-Key | Samsung Electro-Mechanics | CL05A475MO5NUNC
Cap,270pF,50V,10%,X7R,0402 | C9, C10 | C1005[0402] | 2 | 2 | 4 | 1276-1236-1-ND | Digi-Key | Samsung Electro-Mechanics | CL05B271KB5NNNC
Cap,SMD,10nF,25V,10%,X7R,0402 | C11 | C1005[0402] | 1 | 2 | 2 | 1276-1057-1-ND | Digi-Key | Samsung Electro-Mechanics | CL05B103KA5NNNC
GPS Module | U10 | XA1100 | 1 | 2 | 2 | 1645-1094-1-ND | Digi-Key | Sierra Wireless | XA1100_1103872
Res,SMD,4R99,1/4W,5% | R2, R4, R6, R8, R14, R16, R18, R20 | RESC1005X03N | 8 | 2 | 16 | RMCF0402FT4R99CT-ND | Digi-Key | Stackpole | RMCF0402FT4R99
Res,SMD,1/10W,3K16,0603,1% | R28 | R1608[0603] small | 1 | 2 | 2 | RMCF0603FT3K16CT-ND | Digi-Key | Stackpole Electronics | RMCF0603FT3K16
0.100" Female Header | J8 | 0.100" 9PIN | 1 | 2 | 2 | S7042-ND | Digi-Key | Sullins | PPPC091LFBN-RC
DC-DC: 0.9-6V 2A output, 3-17V input. Non-isolated. | U5 | SIL0008D | 1 | 2 | 2 | 296-47089-1-ND | Digi-Key | Texas Instruments | TPS82140SILT
Quad opamplifiers | U1, U2 | SOIC-14 | 2 | 2 | 4 | LMC660CMX/NOPBCT-ND | Digi-Key | Texas Instruments | LMC660CMX/NOPB
22uF 50V Hybrid Polymer Capacitor | C19 | Radial Can F61 6.6x6.6 | 1 | 2 | 2 | 565-4188-6-ND | Digikey | United Chemi-Con | HHXB500ARA220MF61G | update to 565-4188-1-ND for cut-tape instead of digi-reel
LED RGB Clear 624nm/526nm/469nm 2V/3.1V/3V PLCC-6 | D1 | VLMRGB6112 | 1 | 2 | 2 | VLMRGB6112-00-GS08CT-ND | Digi-Key | Vishay Semiconductor Opto Division | VLMRGB6112-00-GS08
Cap,3.3nF,16V,10%,X7R,0402 | C12 | C1005[0402] | 1 | 2 | 2 | 311-3803-1-ND | Digi-Key | Yageo | CC0402KRX7R7BB332
Cap,18pF,50V,5%,C0G/NP0,0402 | C13, C16 | C1005[0402] | 2 | 2 | 4 | 311-1415-1-ND | Digi-Key | Yageo | CC0402JRNPO9BN180
Cap,20pF,50V,5%,C0G/NP0,0402 | C14, C15 | C1005[0402] | 2 | 2 | 4 | 311-1417-1-ND | Digi-Key | Yageo | CC0402JRNPO9BN200
Cap,47pF,50V,5%,C0G/NP0 | C34, C35 | C1005[0402] | 2 | 2 | 4 | 311-1021-1-ND | Digi-Key | Yageo | CC0402JRNPO9BN470
Cap,100pF,10V,5%,C0G/NP0,0402 | C36 | C1005[0402] | 1 | 2 | 2 | 311-1024-1-ND | Digi-Key | Yageo | CC0402JRNPO9BN101
RES 1K Ohm ±5%, 0.25W,1/4W 0603 | R32 | R1608[0603] small | 1 | 2 | 2 | 311-1.20KHRCT-ND | Digi-Key | Yageo | RC0603FR-071K2L
Res,SMD,4K53,1/10W,1%,0603 | R29 | R1608[0603] small | 1 | 2 | 2 | 311-4.53KHRCT-ND | Digi-Key | Yageo | RC0603FR-074K53L
 |  |  |  |  |  |  |  |  | ADD: light pipe, antennas, external sensors
 |  |  |  |  |  |  |  |  | NEED TO REPLACE THE DSB… TEMP SENSOR

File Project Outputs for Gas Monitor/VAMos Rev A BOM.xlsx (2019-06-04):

Designator | Comment | Value | Supplier | Link | DigiKey Part # | Manufacturer | Mfg. Part # | Price @ 1 | Quantity | Total | Total: | $186.86
D10 | High Conductance Fast Diode |  |  | https://www.digikey.ca/products/en?keywords=1N4148W-FDICT-ND | 1N4148W-FDICT-ND | Diodes Incorporated | 1N4148W-7-F | $0.26 | 2 | $0.52
J11 | 301 30mm Coin Cell Holder |  |  | https://www.digikey.ca/product-detail/en/keystone-electronics/301/36-301-ND/303828 | 36-301-ND | Keystone Electronics |  | $2.72 | 1 | $2.72
J2 | 3-pin Terminal Block |  |  | https://www.digikey.ca/products/en?keywords=277-1578-ND | 277-1578-ND | Phoenix Contact | 1935174 | $0.85 | 1 | $0.85
E1 | Antenna |  |  |  |  |  |  |  |  | $0.00
U6 | Digital Environmental Sensor |  |  | https://www.digikey.ca/products/en?keywords=828-1063-1-ND | 828-1063-1-ND | Bosch Sensortec | BME280 | $11.84 | 1 | $11.84
S1,S2 | Switch |  |  | https://www.digikey.ca/products/en?keywords=GPTS203211B | CW181-ND | CW Industries | GPTS203211B | $1.05 | 4 | $4.20
C1,C2,C3,C5,C6,C20,C21,C22,C23,C24,C25,C26,C27,C28,C29,C30,C31,C32,C41 | Capacitor | 0.1uF |  | https://www.digikey.ca/product-detail/en/samsung-electro-mechanics/CL10B104KA8NNNC/1276-1006-1-ND/3889092 | 1276-1006-1-ND | Samsung Electromechanics | CL10B104KA8NNNC | $0.14 | 25 | $3.50
C33,C34,C36,C37,C38,C39,C40,C42,C43,C44,C45 | Capacitor | 4.7uF |  | https://www.digikey.ca/product-detail/en/samsung-electro-mechanics/CL10B475KQ8NQNC/1276-2087-1-ND/3890173 | 1276-2087-1-ND | Samsung Electromechanics | CL10B475KQ8NQNC | $0.24 | 25 | $6.00
C4,C7 | Capacitor | 10uF |  | https://www.digikey.ca/product-detail/en/murata-electronics-north-america/GRM188R61E106MA73D/490-7202-1-ND/3900486 | 490-7202-1-ND | Murata Electronics North America | GRM188R61E106MA73D0 | $0.60 | 10 | $6.00
C8 | Capacitor | 3.3nF = 3300pF 5% |  | https://www.digikey.ca/product-detail/en/samsung-electro-mechanics/CL10B332JB8NNNC/1276-2030-1-ND/3890116 | 1276-2030-1-ND | Samsung Electromechanics | CL10B332JB8NNNC | $0.14 | 5 | $0.70
C9 | Capacitor | 10nF |  | https://www.digikey.ca/product-detail/en/samsung-electro-mechanics/CL10B103JB8NNNC/1276-1103-1-ND/3889189 | 1276-1103-1-ND | Samsung Electromechanics | CL10B103JB8NNNC | $0.14 | 5 | $0.70
C10 | Capacitor | 2.4pF |  | https://www.digikey.ca/product-detail/en/murata-electronics-north-america/GQM1875C2E2R4BB12D/490-11257-1-ND/5333097 | 490-11257-1-ND | Murata Electronics North America | GQM1875C2E2R4BB12D | $1.16 | 5 | $5.80
C11 | Capacitor | 5.6pF |  | https://www.digikey.ca/product-detail/en/murata-electronics-north-america/GQM1875C2E5R6CB12D/490-7162-1-ND/3855078 | 490-7162-1-ND | Murata Electronics North America | GQM1875C2E5R6CB12D | $1.09 | 5 | $5.45
C12,C13 | Capacitor | 270pF |  | https://www.digikey.ca/product-detail/en/samsung-electro-mechanics/CL10B271KB8NNNC/1276-2019-1-ND/3890105 | 1276-2019-1-ND | Samsung Electro-Mechanics | CL10B271KB8NNNC | $0.14 | 10 | $1.40
C14,C15 | Capacitor | 18pF |  | https://www.digikey.ca/product-detail/en/walsin-technology-corporation/0603N180J500CT/1292-1494-1-ND/9355498 | 1292-1494-1-ND | Walsin Technology Corporation | 0603N180J500CT | $0.14 | 10 | $1.40
C16,C17 | Capacitor | 20pF |  | https://www.digikey.ca/product-detail/en/samsung-electro-mechanics/CL10C200JB8NNNC/1276-1187-1-ND/3889273 | 1276-1187-1-ND | Samsung Electro-Mechanics | CL10C200JB8NNNC | $0.14 | 10 | $1.40
C18,C19 | Capacitor | 47pF |  | https://www.digikey.ca/product-detail/en/wurth-electronics-inc/885012006021/732-7764-1-ND/5454391 | 732-7764-1-ND | Wurth Electronics Inc. | 885012006021 | $0.14 | 10 | $1.40
D2,D3,D4,D5,D6,D7,D8,D9 | TVS Diode | 12.9V Clamp 1A |  | https://www.digikey.ca/products/en?keywords=ESD7951ST5GOSCT-ND | ESD7951ST5GOSCT-ND | ON Semiconductor | ESD7951ST5G | $0.72 | 20 | $14.40
U1 | Microcontroller |  |  |  |  |  |  |  |  | $0.00
Y2 | 40MHz Crystal Oscillator |  |  | https://www.digikey.ca/products/en?keywords=SER4045CT-ND | SER4045CT-ND | EPSON | FA-20H 40.0000MF10Z-K3 | $0.71 | 2 | $1.42
FB1,FB2,FB3 | Ferrite Bead | 40 Ohms @ 100MHz |  | https://www.digikey.ca/products/en?keywords=240-2389-1-ND | 240-2389-1-ND | Laird-Signal Integrity Products | MI0805K400R-10 | $0.26 | 6 | $1.56
U4 | USB-UART Interface |  |  | https://www.digikey.ca/products/en?keywords=768-1129-1-ND | 768-1129-1-ND | FTDI, Future Technology Devices International Ltd | FT231XS-R | $3.20 | 1 | $3.20
J6 | Header, 10-pin, Right Angle |  |  | https://www.digikey.ca/product-detail/en/molex/0022053101/WM4308-ND/26705 | WM4308-ND | Molex | 22053101 | $1.49 | 1 | $1.49
J6 | Header, 10-pin, Upright |  |  | https://www.digikey.ca/product-detail/en/molex/0022232101/WM4208-ND/26683 | WM4208-ND | Molex | 22232101 | $0.88 | 1 | $0.88
TP2,TP3,TP4,TP5,TP6,TP7,TP8,TP9,TP10,TP11,TP15,TP17,TP18,TP19,TP21,TP22,TP23,TP24 | Hook Type Test Point THD | Yellow, 1.02mm hole |  | https://www.digikey.ca/product-detail/en/keystone-electronics/5004/36-5004-ND/362669 | 36-5004-ND | Keystone Electronics | 5004 | $0.50 | 20 | $10.00
TP1,TP2 | Hook Type Test Point SMD |  |  | https://www.digikey.ca/product-detail/en/keystone-electronics/5029/36-5029CT-ND/5980631 | 36-5029CT-ND | Keystone Electronics | 5029 | $0.48 | 3 | $1.44
L1 | Inductor | 2.7nH |  | https://www.digikey.ca/products/en?keywords=490-1103-1-ND | 490-1103-1-ND | Murata Electronics North America | LQG18HN2N7S00D | $0.30 | 2 | $0.60
D1 | LED | 3.20mm L x 1.60mm W |  | https://www.digikey.ca/product-detail/en/lite-on-inc/LTST-C230KFKT/160-2025-1-ND/3711400 | 160-2025-1-ND | Lite-On Inc. | LTST-C230KFKT | $0.47 | 2 | $0.94
D1 | LED | 4.50mm L x 1.15mm W |  | https://www.digikey.ca/product-detail/en/stanley-electric-co/CRGB1318FSE-TM/404-1264-1-ND/9477269 | 404-1264-1-ND | Stanley Electric Co. | CRGB1318FSE-TM | $2.18 | 1 | $2.18
U8,U9 | Quad opamplifiers |  |  | https://www.digikey.ca/product-detail/en/texas-instruments/LMC660AIMX/LMC660AIMXTR-ND/3698031 | LMC660CMX/NOPBCT-ND | Texas Instruments | LMC660CMX/NOPB | $3.40 | 2 | $6.80
U15 | Dual NPN Transistors |  |  | https://www.digikey.ca/product-detail/en/on-semiconductor/MBT3904DW1T1G/MBT3904DW1T1GOSCT-ND/918012 | MBT3904DW1T1GOSCT-ND | ON Semiconductor | MBT3904DW1T1G | $0.32 | 1 | $0.32
Y1 | 32.768 kHz Crystal |  |  | https://www.digikey.ca/product-detail/en/epson/MC-146-32.768KA-AC3-ROHS/SER2416CT-ND/1532557 | SER2416CT-ND | EPSON | MC-146 32.768KA-AC3:ROHS | $0.60 | 2 | $1.20
J8 | microSD |  |  | https://www.digikey.ca/product-detail/en/molex/0472192001/WM6698CT-ND/3044147 | WM6698CT-ND | Molex | 472192001 | $1.65 | 1 | $1.65
J4 | 9-pin 0.100" Female Header |  |  | https://www.digikey.ca/product-detail/en/sullins-connector-solutions/PPPC091LFBN-RC/S7042-ND/810181 | S7042-ND | Sullins Connector Solutions | PPPC091LFBN-RC | $0.95 | 1 | $0.95
J1 | Connector 2-pin |  |  | https://www.digikey.ca/product-detail/en/molex/0022232023/WM19468-ND/3157697 | WM19468-ND | Molex | 22232023 | $0.35 | 1 | $0.35
D11 | Shottky Diode |  |  | https://www.digikey.ca/product-detail/en/on-semiconductor/RB521S30T1G/RB521S30T1GOSCT-ND/964627 | RB521S30T1GOSCT-ND | ON Semiconductor | RB521S30T1G | $0.26 | 1 | $0.26
R1,R3,R4,R5,R6, | Resistor | 20K 5%, 0805 |  | https://www.digikey.ca/product-detail/en/stackpole-electronics-inc/RMCF0805JT20K0/RMCF0805JT20K0CT-ND/1942580 | RMCF0805JT20K0CT-ND | Stackpole Electronics Inc. | RMCF0805JT20K0 | $0.15 | 10 | $1.50
R2 | Resistor | 499R |  | https://www.digikey.ca/product-detail/en/stackpole-electronics-inc/RMCF0805FT499R/RMCF0805FT499RCT-ND/1942358 | RMCF0805FT499RCT-ND | Stackpole Electronics Inc. | RMCF0805FT499R | $0.15 | 10 | $1.50
R3 | Resistor | 0R |  | https://www.digikey.ca/product-detail/en/bourns-inc/CR0805-J-000ELF/CR0805-J-000ELFCT-ND/3592913 | CR0805-J/-000ELFCT-ND | Bourns Inc. | CR0805-J/-000ELF | $0.15 | 10 | $1.50
R4,R5,R12,R13,R45,R46,R47,R48,R49,R50 | Resistor | 10K 5%, 0805 |  | https://www.digikey.ca/product-detail/en/bourns-inc/CR0805-JW-103ELF/CR0805-JW-103ELFCT-ND/3592918 | CR0805-JW-103ELFCT-ND | Bourns Inc. | CR0805-JW-103ELF | $0.15 | 25 | $3.75
R6 | Resistor | 330R 5%, 0805 |  | https://www.digikey.ca/product-detail/en/stackpole-electronics-inc/RMCF0805JT330R/RMCF0805JT330RCT-ND/1942547 | RMCF0805JT330RCT-ND | Stackpole Electronics Inc. | RMCF0805JT330R | $0.15 | 10 | $1.50
R7,R8 | Resistor | 27R, 0603 |  | https://www.digikey.ca/product-detail/en/stackpole-electronics-inc/RMCF0603JT27R0/RMCF0603JT27R0CT-ND/2418191 | RMCF0603JT27R0CT-ND | Stackpole Electronics Inc. | RMCF0603JT27R0 | $0.15 | 10 | $1.50
R9,R10,R11 | Resistor | 22R 5%, 0805 |  | https://www.digikey.ca/product-detail/en/stackpole-electronics-inc/RMCF0805JT22R0/RMCF0805JT22R0CT-ND/1942533 | RMCF0805JT22R0CT-ND | Stackpole Electronics Inc. | RMCF0805JT22R0 | $0.15 | 10 | $1.50
R14,R15,R16,R17,R18,R19,R22,R25,R28,R31,R34,R37,R40,R44 | Resistor | 1K 5%, 0805 |  | https://www.digikey.ca/product-detail/en/bourns-inc/CR0805-JW-102ELF/CR0805-JW-102ELFCT-ND/3592930 | CR0805-JW-102ELFCT-ND | Bourns Inc. | CR0805-JW-102ELF | $0.15 | 25 | $3.75
R20,R23,R26,R29,R32,R35,R38,R41 | Resistor | 4R99 1%, 0805 |  | https://www.digikey.ca/product-detail/en/stackpole-electronics-inc/RMCF0805FT4R99/RMCF0805FT4R99CT-ND/2418423 | RMCF0805FT4R99CT-ND | Stackpole Electronics Inc. | RMCF0805FT4R99 | $0.15 | 25 | $3.75
R21,R24,R27,R30,R33,R36,R39,R42 | Resistor | 22K 5%, 0805 |  | https://www.digikey.ca/product-detail/en/stackpole-electronics-inc/RMCF0805JT22K0/RMCF0805JT22K0CT-ND/1942581 | RMCF0805JT22K0CT-ND | Stackpole Electronics Inc. | RMCF0805JT22K0 | $0.15 | 25 | $3.75
R43 | Resistor | 100K %5 0.5W |  | https://www.digikey.ca/product-detail/en/vishay-bc-components/SFR16S0001003JR500/BC4296CT-ND/7351726 | BC4296CT-ND | Vishay BC Components | SFR16S0001003JR500 | $0.20 | 2 | $0.40
U2 | QSPI 128M Flash Memory |  |  | https://www.digikey.ca/product-detail/en/cypress-semiconductor-corp/S25FL128SDPMFIG10/428-4172-ND/3862707 | 428-4172-ND | Cypress Semiconductor Corp | S25FL128SDPMFIG10 | $4.91 | 1 | $4.91
J5 | uFl Connector |  |  | https://www.digikey.ca/products/en?keywords=CONUFL001-SMD-TCT-ND | CONUFL001-SMD-TCT-ND | Linx Technologies Inc. | CONUFL001-SMD-T | $0.64 | 1 | $0.64
U3 | USB Shield |  |  | https://www.digikey.ca/products/en?keywords=102-4007-1-ND | 102-4007-1-ND | CUI Inc. | UJ2-MIBH2-4-SMT-TR | $1.45 | 1 | $1.45
J3 | Connector 3-pin |  |  | https://www.digikey.ca/product-detail/en/molex/0022232031/WM4201-ND/26669 | WM4201-ND | Molex | 22232031 | $0.34 | 1 | $0.34
U7 | GPS Module |  |  | https://www.digikey.ca/products/en?keywords=1645-1094-1-ND | 1645-1094-1-ND | Sierra Wireless | XA1100_1103872 | $27.64 | 1 | $27.64
U10,U11,U12,U13 | Linear Regulator 1A | 3.3V, Factory Stock |  | https://www.digikey.ca/product-detail/en/diodes-incorporated/ZLDO1117QG33TA/ZLDO1117QG33TADICT-ND/8545998 | ZLDO1117QG33TADICT-ND | Diodes Incorporated | ZLDO1117QG33TA | $0.94 | 5 | $4.70
U15 | Linear Regulator 1A | 5V, Factory Stock |  | https://www.digikey.ca/product-detail/en/diodes-incorporated/ZLDO1117G50TA/ZLDO1117G50DICT-ND/2095613 | ZLDO1117G50DICT-ND | Diodes Incorporated | ZLDO1117G50TA | $0.76 | 1 | $0.76
D12 | Power Diode |  |  | https://www.digikey.ca/product-detail/en/micro-commercial-co/1N4007-TP/1N4007-TPMSCT-ND/773694 | 1N4007-TPMSCT-ND | Micro Commercial Co | 1N4007-TP | $0.16 | 1 | $0.16
L2 | Power Inductor | 500uH |  | https://www.digikey.ca/products/en/inductors-coils-chokes/fixed-inductors/71?k=inductor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 | HM3330-ND | Hammond Manufacturing | 1536Y | $3.69 | 1 | $3.69
C35 | Capacitor | 47uF 50V |  | https://www.digikey.ca/product-detail/en/nichicon/UFW1H470MED1TD/493-11014-1-ND/4317921 | 493-11014-1-ND | Nichicon | UFW1H470MED1TD | $0.40 | 1 | $0.40
Q3 | N-Channel MOSFET | 100V 10A 48W |  | https://www.digikey.ca/product-detail/en/infineon-technologies/IRL520NPBF/IRL520NPBF-ND/811770 | IRL520NPBF-ND | Infineon Technologies | IRL520NPBF | $1.42 | 1 | $1.42
J7 | 6-pin 0.100" Male Header |  |  | https://www.digikey.ca/product-detail/en/molex/0022232061/WM4204-ND/26675 | WM4204-ND | Molex | 22232061 | $0.61 | 1 | $0.61 |  | wrong, need wider spaced one
 | Capacitor | 10uF THD |  | https://www.digikey.ca/product-detail/en/tdk-corporation/FG16X7R1E106KRT06/445-173156-1-ND/5811761 | 445-173156-1-ND | TDK Corporation | FG16X7R1E106KRT06 | $1.08 | 10 | $10.80
 | Linear Regulator 800mA THD |  |  | https://www.digikey.ca/product-detail/en/on-semiconductor/MC33269T-3.3G/MC33269T-3.3GOS-ND/920880 | MC33269T-3.3GOS-ND | ON Semiconductor | MC33269T-3.3G | $1.42 | 1 | $1.42
 | mistakes
 | TP holes too small
 | J7 footprint too large of pitch
 | U4 footprint too wide
 | bme footprint pins misordered
 | coin cell holder too big, footprint doesn't have through-holes
 | J2 terminal block holes too small, footprint didn't have silkscreen so too close to components (kevin!!!)

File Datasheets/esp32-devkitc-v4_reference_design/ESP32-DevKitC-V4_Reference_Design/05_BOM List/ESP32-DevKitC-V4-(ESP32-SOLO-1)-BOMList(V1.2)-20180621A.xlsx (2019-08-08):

ESP32-DevKitC-V4 BOMList(V1.2)
ID | Qty | Ref Des | Value | Package | ICs | Description
1 | 3 | C1, C3, C21 | 22 uF/10V (20%) | 0603 | Capacitor | Ceramic Capacitor
2 | 4 | C9, C14, C19, C22 | 0.1 uF/50V (10%) | 0402 | Capacitor | Ceramic Capacitor
3 | 1 | C20 | 4.7 uF/6.3V (10%) | 0402 | Capacitor | Ceramic Capacitor
4 | 1 | D1 | RED LED | 0603 | Diode | light-emitting diode: Red
5 | 1 | D2 | ESP-WROOM-32 | ESP32_MODULE | Module | ESP32-SOLO-1 (3.3V 32 Mbit)
6 | 1 | D3 | BAT760-7 | SOD323 | Diode | Schottky Diode, Vrrm=30V, Vr=21V, I=1A, IFSM=5.5A
7 | 3 | D4, D5, D6 | LESD5D5.0CT1G | SOD-523 | Diode | ESD, TVS Diode, 5V
8 | 1 | J1 | Micro USB Type B Female 5 Pin DIP/插件 | USB_5P | Connector | Micro USB
9 | 2 | Q1, Q2 | S8050 | SOT-23-3 | Transistor | Transistor
10 | 2 | R2, R24 | 2K (5%) | 0402 | Resistor | Chip Resistors
11 | 3 | R11, R21, R22 | 10K (5%) | 0402 | Resistor | Chip Resistors
12 | 2 | R17, R18 | 0R (5%) | 0402 | Resistor | Chip Resistors
13 | 1 | R25 | 22.1K (5%) | 0402 | Resistor | Chip Resistors
14 | 1 | R26 | 47.5K (5%) | 0402 | Resistor | Chip Resistors
15 | 2 | SW1, SW2 | SW push button | Tact Switch | Tact Switch | 复位按键，2 脚，3x4x2，贴片 (reset button, 2-pin, 3x4x2, SMT)
16 | 2 | J2, J3 | CON19X1_2P54 | CON19_2P54 | Connector | Male PCB Single Row Straight Header Connector, 2.54 mm Pitch, 19 Pins
17 | 1 | U1 | CP2102N-A01-GQFN28 | CP2102_QFN_28P | Interface ICs | USB-to-UART, USB2.0 full speed, data rate up to 3M baud
18 | 1 | U2 | AMS1117-3.3 | SOT-223 | Power ICs | LDO, 5V 转 3.3V 固定输出, 1A, SOT-223 (LDO, 5V/3.3V, 1A, SOT-223)

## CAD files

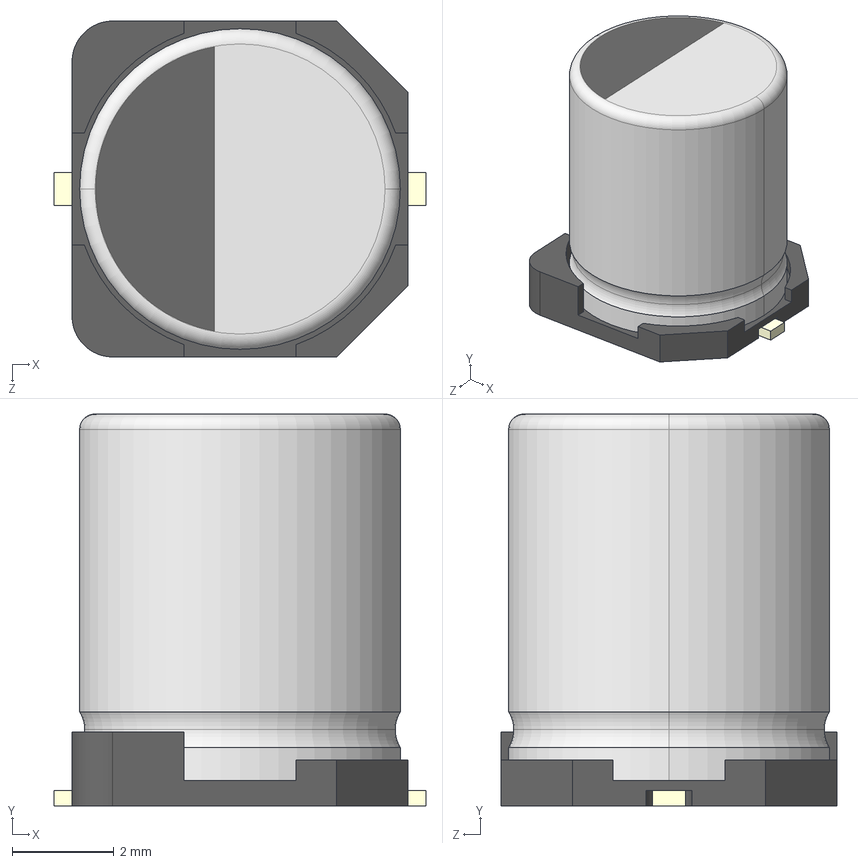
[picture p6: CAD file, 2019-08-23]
3D Models/DS_Alumi_D8/DS_Alumi_D8/â│6.3 SIZE CODE D8.stp
7.30 x 7.70 x 6.60 mm
標準SIZE CODE D8-001
標準SIZE CODE D8-002
標準SIZE CODE D8-003 x 2

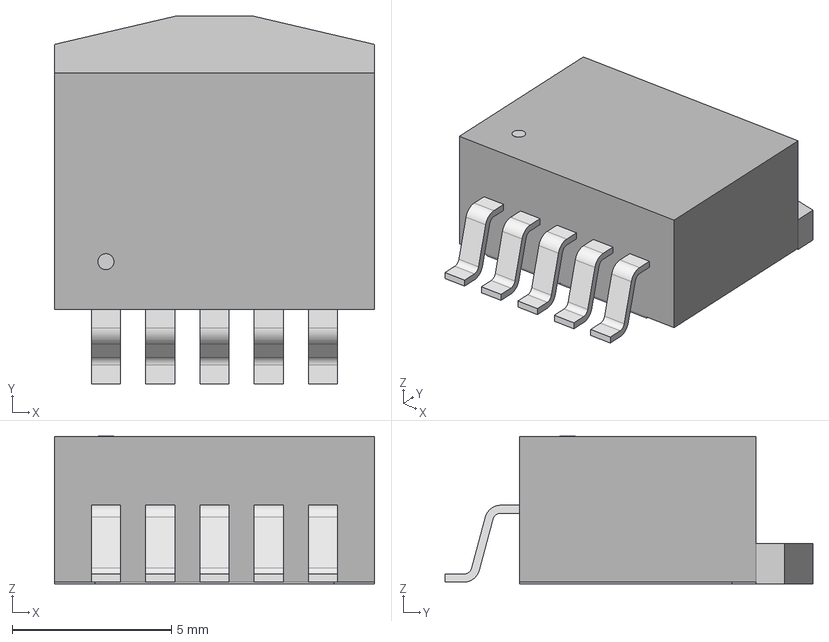
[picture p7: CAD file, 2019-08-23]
3D Models/UL_NCP57302DSADJR4G/2019-08-23_07-21-21/STEP/D2PAK-5-L.step
10.0 x 11.5 x 4.63 mm

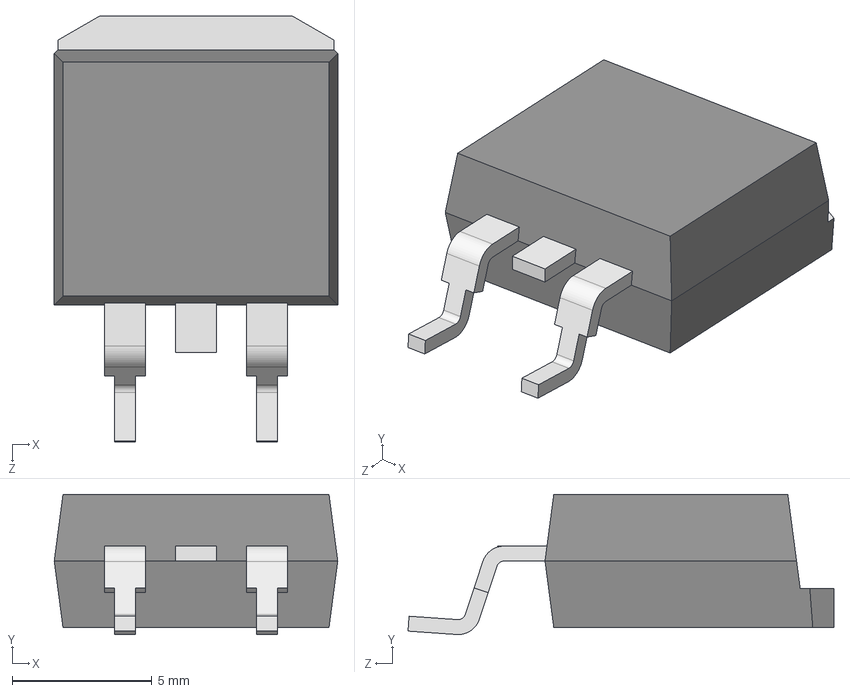
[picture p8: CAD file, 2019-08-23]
3D Models/D2PAK.step
10.2 x 5.02 x 15.3 mm

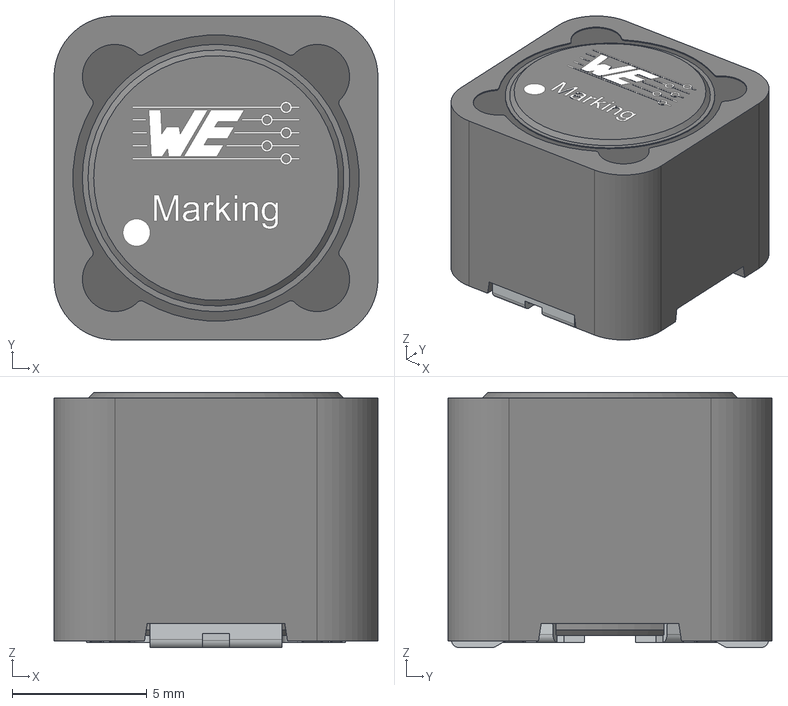
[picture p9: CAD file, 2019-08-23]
3D Models/WE-PD-1210-rev1.stp
12.0 x 12.0 x 9.46 mm
Core
ShieldRing
Glue
Leadframe

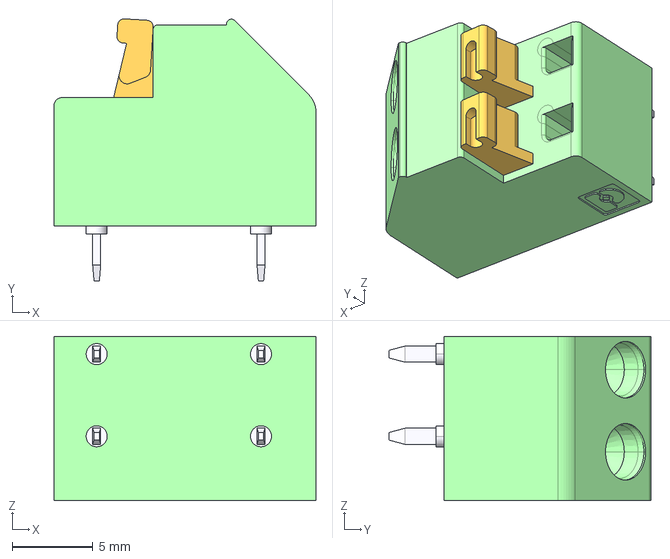
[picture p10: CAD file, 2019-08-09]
3D Models/pxc_1790283_03_MFKDSP-2-5-08_3D.stp
16.2 x 16.2 x 10.2 mm

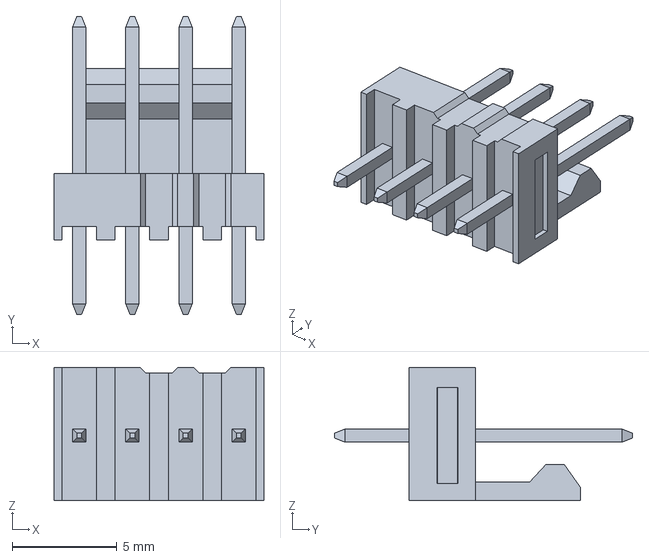
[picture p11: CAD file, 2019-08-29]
3D Models/022232041.stp
10.0 x 14.2 x 6.35 mm

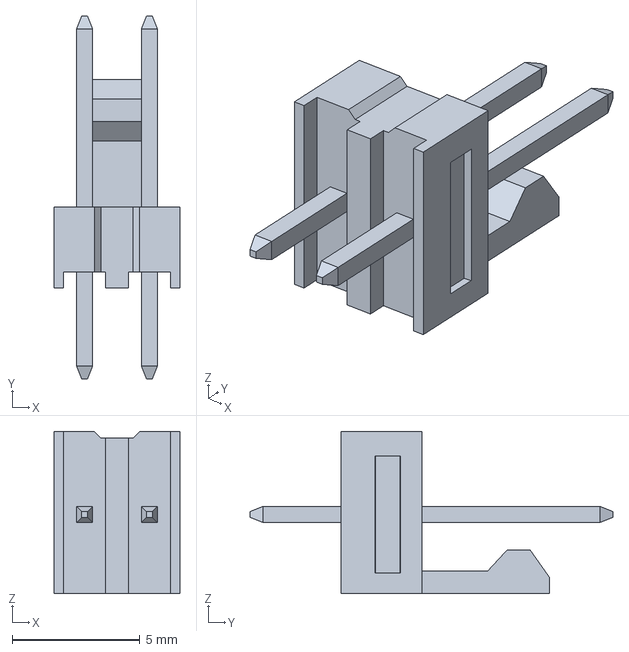
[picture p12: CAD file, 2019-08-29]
3D Models/022232021.stp
4.93 x 14.2 x 6.35 mm

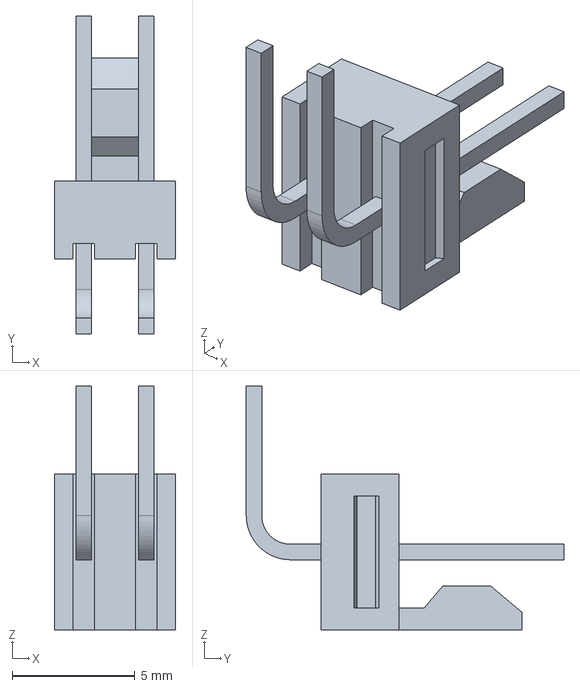
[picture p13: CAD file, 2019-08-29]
3D Models/022053021.stp
4.93 x 12.9 x 9.93 mm

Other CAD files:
3D Models/UL_NCP57302DSADJR4G/2019-08-23_07-21-21/STEP/D2PAK-5-M.step
3D Models/UL_NCP57302DSADJR4G/2019-08-23_07-21-21/STEP/D2PAK-5.step

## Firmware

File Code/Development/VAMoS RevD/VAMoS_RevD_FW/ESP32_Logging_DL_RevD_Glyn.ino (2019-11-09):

/*
 * Logs all data from environmental sensors to SD card hosts a web server for data download
 * Includes analog sensors, outputs them to SD card in ADC values
 * Runs the set cycle time for warmup, active, and sleep
 * 
 * Last tested: 12-Sept-2019 with VAMoS RevD
 */

// Libraries for SD card
#include "FS.h"
#include "SD.h"
#include <SPI.h>

//DS18B20 libraries
#include <OneWire.h>            // https://github.com/PaulStoffregen/OneWire
#include <DallasTemperature.h>  // https://github.com/milesburton/Arduino-Temperature-Control-Library

// Libraries to get time from NTP Server
#include <WiFi.h>
#include <NTPClient.h>          // https://github.com/taranais/NTPClient
#include <WiFiUdp.h>

#include <Wire.h>

// HIH6120 library
#include <HIH61XX.h>

// GPS library
#include <Adafruit_GPS.h>

// BME280 libraries
#include <Adafruit_Sensor.h>
#include <Adafruit_BME280.h>

// Wifi and web server libraries
#include <WiFi.h>
#include <ESP32WebServer.h>         // https://github.com/Pedroalbuquerque/ESP32WebServer
#include <ESPmDNS.h>                // From ESP package
// Web server header files
#include "ESP32_Logging_DL_vars.h"
#include "ESP32_Logging_DL_css.h"

// Define deep sleep options
uint64_t uS_TO_S_FACTOR = 1000000;  // Conversion factor for micro seconds to seconds
// Sleep for 1 minutes = 60 seconds
uint64_t TIME_TO_SLEEP = 15;

// Define CS pin for the SD card module
#define SD_CS 5

#define BME_SCK 22
//#define BME_MISO 12
#define BME_MOSI 21
//#define BME_CS 10

Adafruit_BME280 bme; // I2C

#define SEALEVELPRESSURE_HPA (1013.25)
#define PUMP 26
#define ALPHS_EN 13
//#define WARMUP_TIME 1800000 // 30 mins to warm up sensors (could be reduced to 25 mins)
#define WARMUP_TIME 5000 // 5 seconds to warm up sensors (should be 25 mins)
#define ACTIVE_TIME 60000 // 30 seconds
//#define ACTIVE_TIME 300000 // 5 mins
#define PUMP_MAX_DUTY_MIN_TIME 3000 // 3 seconds for pump to run at 100% duty cycle
#define GREEN 32
#define RED 33

// Save reading number on RTC memory
RTC_DATA_ATTR int readingID = 0;
RTC_DATA_ATTR int fileNumber = 0;

String dataMessage;

// Create an HIH61XX with I2C address 0x27, powered by 3.3V pin
HIH61XX hih(0x27);

// Data wire is connected to ESP32 GPIO 27
#define ONE_WIRE_BUS 27
// Setup a oneWire instance to communicate with a OneWire device
OneWire oneWire(ONE_WIRE_BUS);
// Pass our oneWire reference to Dallas Temperature sensor 
DallasTemperature sensors(&oneWire);

/***** GPS DEFINITIONS ****/
#define GPSSerial Serial2
#define RXD2 16
#define TXD2 17
// Connect to the GPS on the hardware port
Adafruit_GPS GPS(&GPSSerial);
// Set GPSECHO to 'false' to turn off echoing the GPS data to the Serial console
// Set to 'true' if you want to debug and listen to the raw GPS sentences
#define GPSECHO false

uint32_t timer = millis();
uint32_t start_time = millis();
uint32_t active_start_time = millis();
uint32_t pump_max_duty_start_time = millis();
int delayTime = 1000;
int GPSwait = 3000;
bool warm_init_flag = 0;            // Flag so warm up only runs once per wakeup
bool active_init_flag = 0;          // Flag so pump runs 100% duty cycle only once (when it enters active mode)

// Environmental Sensor variables
float DS18B20_temp;
float bme_t;
float bme_rh;
float bme_p;
float hih_rh;
float hih_t;

// Analog sensor variables
#define ALPHS1 35
#define ALPHS2 2
#define ALPHS3 12
#define ALPHS4 4
#define ALPHS5 34
#define ALPHS6 36
#define ALPHS7 39
#define ALPHS8 25

// Analog sensor variables
int ALPHS1_ADC;
int ALPHS2_ADC;
int ALPHS3_ADC;
int ALPHS4_ADC;
int ALPHS5_ADC;
int ALPHS6_ADC;
int ALPHS7_ADC;
int ALPHS8_ADC;

float ALPHS1_volts;
float ALPHS2_volts;
float ALPHS3_volts;
float ALPHS4_volts;
float ALPHS5_volts;
float ALPHS6_volts;
float ALPHS7_volts;
float ALPHS8_volts;

// Parameters for pump PWM
const int freq = 500;
const int channel = 0;
const int resolution = 8;

// Define NTP Client to get time
// VIV'S NOTE: Will we actually have access to an NTP server on the glacier?
// Probably not, hence will have to use the GPS
WiFiUDP ntpUDP;
NTPClient timeClient(ntpUDP);

// Variables to save date and time
String formattedDate;
String dayStamp;
String timeStamp;

// Initialize server at port 80
ESP32WebServer  server(80);

void setup() {
  // Start serial communication for debugging purposes
  Serial.begin(115200);
  pinMode(PUMP,OUTPUT);
  ledcSetup(channel, freq, resolution);
  ledcAttachPin(PUMP, channel);

  pinMode(GREEN,OUTPUT);
  pinMode(RED,OUTPUT);

  pinMode(ALPHS1,INPUT);
  pinMode(ALPHS2,INPUT);
  pinMode(ALPHS3,INPUT);
  pinMode(ALPHS4,INPUT);
  pinMode(ALPHS5,INPUT);
  pinMode(ALPHS6,INPUT);
  pinMode(ALPHS7,INPUT);
  pinMode(ALPHS8,INPUT);
  
  pinMode(ALPHS_EN,OUTPUT); // set enable pin as output  
  ledcWrite(channel,255); // set pump to max duty cycle
  delay(3000); // keep high for 3 seconds
  ledcWrite(channel,0); // turn off pump
  
  // Note the format for setting a serial port is as follows:
  //Serial2.begin(baud-rate, protocol, RX pin, TX pin);
  Serial2.begin(115200, SERIAL_8N1, RXD2, TXD2);

    // uncomment this line to turn on RMC (recommended minimum) and GGA (fix data) including altitude
    GPS.sendCommand(PMTK_SET_NMEA_OUTPUT_RMCGGA);
    // Set the update rate
    GPS.sendCommand(PMTK_SET_NMEA_UPDATE_1HZ); // 1 Hz update rate
    // For the parsing code to work nicely and have time to sort thru the data, and
    // print it out we don't suggest using anything higher than 1 Hz
    
    // Request updates on antenna status, comment out to keep quiet
    GPS.sendCommand(PGCMD_ANTENNA);
    delay(delayTime);

    // Setup access point
    Serial.print("Setting AP (Access Point)...");
    WiFi.softAP(ssid, password);

    IPAddress IP = WiFi.softAPIP();
    Serial.print("AP IP address: ");
    Serial.println(IP);

    // Web server setup
    server.on("/",          HomePage);
    server.on("/download",  File_Download);

    server.begin();
    Serial.println("HTTP server started");

    digitalWrite(ALPHS_EN, HIGH);
}

void loop() {
  
  // Enable Timer wake_up
    esp_sleep_enable_timer_wakeup(TIME_TO_SLEEP * uS_TO_S_FACTOR);
    start_time = millis();

    // Set init flags to 0 on wake
    warm_init_flag = 0;
    active_init_flag = 0;

    // Begin handle client loop
    while(millis() - start_time < WARMUP_TIME + ACTIVE_TIME)
    {
        // Sensor functions
        // If statements are used because we need to run SendHTML functions with every loop
        if (millis() - start_time < WARMUP_TIME)
        {
            warmSensor();

            // Set active start_time at the end of the warmup time
            // Active time won't run unless warmup is already done (else if statement)
            active_start_time = millis();
        }
        else if (millis() - active_start_time < ACTIVE_TIME)
            runSensor();

        // HTTP stuff
        server.handleClient();
    }

    // Go back to deep sleep
    Serial.println("Done! Going to sleep now.");

    digitalWrite(ALPHS_EN, LOW);

    // Turn off pump
    ledcWrite(channel, 0);   

    digitalWrite(GREEN, HIGH);
    digitalWrite(RED, HIGH);

    delay(500);

    esp_deep_sleep_start();

    // END MAIN LOOP
  
}


//-----------------------------------------------------------------------------
// FUNCTIONS
//-----------------------------------------------------------------------------

//-----------------------------------------------------------------------------
// Peripheral functions
//-----------------------------------------------------------------------------

void initializeSD(){
  // Initialize SD card
  SD.begin(SD_CS);  
  if(!SD.begin(SD_CS)) {
    Serial.println("Card Mount Failed");
    return;
  }
  uint8_t cardType = SD.cardType();
  if(cardType == CARD_NONE) {
    Serial.println("No SD card attached");
    return;
  }
  Serial.println("Initializing SD card...");
  if (!SD.begin(SD_CS)) {
    Serial.println("ERROR - SD card initialization failed!");
    return;    // init failed
  }
}

// Function to get temperature
void DS18B20_Readings(){
  sensors.requestTemperatures(); 
  DS18B20_temp = sensors.getTempCByIndex(0); // Temperature in Celsius
  //temperature = sensors.getTempFByIndex(0); // Temperature in Fahrenheit
  Serial.print("DS18B20 Temp: ");
  Serial.println(DS18B20_temp);
}

void BME280_Readings() {
    Serial.print("BME280 Temperature = ");
    bme_t = bme.readTemperature();
    Serial.print(bme_t);
    Serial.println(" *C");

    Serial.print("BME280 Pressure = ");
    bme_p = bme.readPressure() / 100.0F;
    Serial.print(bme_p);
    Serial.println(" hPa");

    Serial.print("BME280 Approx. Altitude = ");
    Serial.print(bme.readAltitude(SEALEVELPRESSURE_HPA));
    Serial.println(" m");

    Serial.print("BME280 Humidity = ");
    bme_rh = bme.readHumidity();
    Serial.print(bme_rh);
    Serial.println(" %");

    Serial.println();
}

void HIH6120_Readings(){
    hih.update();
    
    Serial.print("HIH6120 Humidity: ");
    hih_rh = hih.humidity()*100;
    Serial.print(hih_rh, 5);
    Serial.println(" %");
    Serial.print("HIH6120 RH Raw: ");
    Serial.println(hih.humidity_Raw());
    
    Serial.print("Ext HIH Temperature: ");
    hih_t = hih.temperature();
    Serial.print(hih_t, 5);
    Serial.println(" *C");
    Serial.print("HIH6120 Temp Raw: ");
    Serial.println(hih.temperature_Raw());

    Serial.println();
}

// Function to get date and time from NTPClient
void getTimeStamp() {
  while(!timeClient.update()) {
    timeClient.forceUpdate();
  }
  // The formattedDate comes with the following format:
  // 2018-05-28T16:00:13Z
  // We need to extract date and time
  formattedDate = timeClient.getFormattedDate();
  Serial.println(formattedDate);

  // Extract date
  int splitT = formattedDate.indexOf("T");
  dayStamp = formattedDate.substring(0, splitT);
  Serial.println(dayStamp);
  // Extract time
  timeStamp = formattedDate.substring(splitT+1, formattedDate.length()-1);
  Serial.println(timeStamp);
}

// Write the sensor readings on the SD card
void logSDCard() {
  //dataMessage = String(readingID) + "," + String(dayStamp) + "," + String(timeStamp) + "," + String(temperature) + "\r\n";
  dataMessage = String(readingID) + "," + String(GPS.day) + "-" + String(GPS.month) + "-" + String(GPS.year) + "," + String(GPS.hour) + ":" + String(GPS.minute) + ":" + String(GPS.seconds) + ":" + String(GPS.milliseconds) + "," 
  + String(DS18B20_temp) + "," + String(bme_t) + "," + String(hih_t) + "," + String(bme_rh) + "," + String(hih_rh) + "," + String(bme_p) + "," + String(ALPHS1_ADC) + "," + String(ALPHS2_ADC) + "," + String(ALPHS3_ADC) + "," + String(ALPHS4_ADC) + ","
  + String(ALPHS5_ADC) + "," + String(ALPHS6_ADC) + "," + String(ALPHS7_ADC) + "," + String(ALPHS8_ADC) + "\r\n";
  Serial.print("Save data: ");
  Serial.println(dataMessage);
  appendFile(SD, "/VAMoS_EnvData.txt", dataMessage.c_str());
}

// Write to the SD card (DON'T MODIFY THIS FUNCTION)
void writeFile(fs::FS &fs, const char * path, const char * message) {
  Serial.printf("Writing file: %s\n", path);

  File file = fs.open(path, FILE_WRITE);
  if(!file) {
    Serial.println("Failed to open file for writing");
    return;
  }
  if(file.print(message)) {
    Serial.println("File written");
  } else {
    Serial.println("Write failed");
  }
  file.close();
}

// Append data to the SD card (DON'T MODIFY THIS FUNCTION)
void appendFile(fs::FS &fs, const char * path, const char * message) {
  Serial.printf("Appending to file: %s\n", path);

  File file = fs.open(path, FILE_APPEND);
  if(!file) {
    Serial.println("Failed to open file for appending");
    return;
  }
  if(file.print(message)) {
    Serial.println("Message appended");
  } else {
    Serial.println("Append failed");
  }
  file.close();
}
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

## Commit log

2019-04-06 [PROJECT] Rev. A. Project File
    [Gas Monitor.PrjPcb]
2019-04-06 [SCHEMATIC] Rev. A. Schematics
    MCU - Configuration of the ESP32 with microSD card connector, antenna matching, and 3.3V regulator
    Amplifiers - Op-amps for amplifying the 4-20mA gas sensor outputs into a 0.6-2.3V voltage signal range
    Pressure, GPS, Temp Sensors - Configuration of the BME280 environmental sensor, XA1100 GPS module, DSB180 temperature probe, and their 3.3V regulators
    USB to Serial - FTDI UART handshake controller and bootloader circuit
    [Amplifiers.SchDoc, MCU.SchDoc, Pressure, GPS, Temp Sensors.SchDoc, USB to Serial.SchDoc]
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2019-04-06 [PCB Libary] Gas Monitor Footprint Library
    [Gas Monitor Components.PcbLib]
2019-04-06 Delete Voltage and Charge Control.SchDec
    Obsolete.
    [Voltage and Charge Control.SchDoc]
2019-04-06 Delete Voltage Regulator and Battery Charger.SchDoc
    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
    [Voltage Regulator and Battery Charger.SchDoc]
2019-04-06 Delete VDB Linear Regulators.SchDoc
    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
    [VDB Linear Regulators.SchDoc]
2019-04-06 Delete Pump Drive.SchDoc
    Obsolete. Moved to separate project.
    [Pump Drive.SchDoc]
2019-04-06 Delete Connectors.SchDoc
    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
    [Connectors.SchDoc]
2019-04-06 Delete 18650 Charging.SchDoc
    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
    [18650 Charging.SchDoc]
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2019-05-21 [SCHEMATIC] Organize into top and subsheets. Remove redundant net labels and subcircuits. Edit FB symbol. Remove some test points.
    [Gas Monitor Components.SchLib]
2019-05-21 [SCHEMATIC] Remove redundant net labels
    Add top sheet, rearrange schematics to include separate Power Supply .SchDoc
    [Amplifiers.SchDoc, Gas Monitor.PrjPcb, GasMonitor5.PcbDoc, Microcontroller.SchDoc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]
2019-05-21 [SCH] minor aesthetic changes
    [Microcontroller.SchDoc, Power Supply.SchDoc, Sensors.SchDoc, USB-UART.SchDoc]
2019-05-21 save project structure
    [Gas Monitor.PrjPcb]
2019-05-23 [SCH] change VDD_SDIO to power net + cosmetic changes
    [Microcontroller.SchDoc]
2019-05-23 [SCH] cleanup sensor doc
    [Sensors.SchDoc]
2019-05-23 [SCH] usb-uart doc cleanup + sheet resize
    [USB-UART.SchDoc]
2019-05-23 [SCH] cleanup
    [Amplifiers.SchDoc, Power Supply.SchDoc, Sensors.SchDoc]
2019-05-23 [SCH] break up and resize
    [Amplifiers.SchDoc]
2019-05-26 [SCH] Clean up top sheet, add connections
    [VAMoS Top Sheet.SchDoc]
2019-05-26 [SCH] Create LDO for each rail, add BUCKOUT port
    Separate 3V3 for VDDIO and then sensors + ESP32. 5V for amplifiers. 12V not shown -- to be added to Hunter's solar charging schematic.
    [Power Supply.SchDoc]
2019-05-26 [SCH] Compile and fix floating power, add note
    [Amplifiers.SchDoc]
2019-05-26 [SCH] Remove redundant ports, add net labels
    [USB-UART.SchDoc]
2019-05-26 [SCH] Update components from new library
    [Sensors.SchDoc]
2019-05-26 [SCHLIB] Create new schematic libraries
    [Capacitors.SchLib, Connectors.SchLib, Diodes.SchLib, ICs.SchLib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]
2019-05-26 [PCBLIB] Fix my footprint fuckups, separate libraries
    [Connectors.PcbLib, ICs.PcbLib, PMIC.PcbLib, Sensors.PcbLib]
2019-05-26 [SCH] Remove rendundant ports
    [Microcontroller.SchDoc]
2019-05-26 [PRJ] Add project files
    [Gas Monitor.PrjPcb, VAMoS PCB.PcbDoc]
2019-06-02 [SCHLIB] Add work libraries
    Libraries without the -V attached are from TZOA. Libraries with the -V appended are made by Vivienne.
    [Active.SchLib, Capacitors.SchLib, Connectors.SchLib, DFM_Features.SchLib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]
2019-06-02 [SCHLIB] Change names of -V libraries
    [Connectors-V.SchLib, ICs-V.SchLib, PMIC-V.SchLib]
2019-06-02 [SCH] Remove VDDIO LDO
    [Power Supply.SchDoc]
2019-06-02 [SCH] Change to signal ground
    [Microcontroller.SchDoc]
2019-06-02 [SCH] Add external RH sensor
    Made a schematic symbol for it in Connectors.SchLib
    [Sensors.SchDoc]
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2019-06-11 [SCH] Replace caps and res with 0603 lib model
    [Amplifiers.SchDoc, Microcontroller.SchDoc, Power Supply.SchDoc, Sensors.SchDoc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]
2019-06-11 [PCB] Create PCB doc with proper footprints
    Missing antenna footprint because it doesn't exist
    [VAMoS PCB RevB.PcbDoc]
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2019-06-19 [SCH] Fix short on microSD lines
    [Microcontroller.SchDoc]
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2019-06-21 [SCH,LIB] Fixing footprints & compiler errors
    [Connectors-V.PcbLib, Connectors-V.SchLib, Gas Monitor.PrjPcb, Microcontroller.SchDoc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]
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2019-06-23 [PCBDOC] Place all components, fix footprints
    [VAMoS PCB RevB.PcbDoc]
2019-06-23 [SCH] Update part numbers, small fixes
    [Microcontroller.SchDoc, Power Supply.SchDoc, Sensors.SchDoc, USB-UART.SchDoc]
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2019-07-03 Fixed resistor values on TPS82140 circuit, ensured that all components on Power Supply schematic have Supplier Part Number 1
    [Power Supply.SchDoc]
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2019-07-05 Fix short on BME280 resistor array chip
    Route more of the MCU and signal lines
    [Connectors-V.SchLib, ICs-V.SchLib, Microcontroller.SchDoc, Microcontrollers.SchLib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]
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2019-07-12 [PCB] Finish routing signals, add vias for power & GND
    Still need to pour polygons and resolve DRC errors
    [Gas Monitor.PrjPcb, VAMoS PCB RevB.PcbDoc]
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2019-07-15 Added some part numbers, fixed BME280
    [Sensors.SchDoc, VAMoS PCB RevB.PcbDoc]
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2019-07-17 [PCB] Add noise reduction inductors to GPS module
    Route noise reduction passives to GPS, impedance match 50 Ohm trace for EXT_ANT, route signals for 2.4GHz WiFi antenna (NOT IMPEDANCE MATCHED YET), add vias for MCU 3V3
    [Inductors.SchLib, Sensors.SchDoc, VAMoS PCB RevB.PcbDoc]
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2019-07-18 [PCB] Fixed unrouted ground nets
    [VAMoS PCB RevB.PcbDoc]
2019-07-18 [PCB] Fixed all unrouted net constraints
    [VAMoS PCB RevB.PcbDoc]
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2019-07-18 Fixed all overlapping part number BOM issues
    [Amplifiers.SchDoc, Gas Monitor.PrjPcb, MCU A.SchDoc, MCU B.SchDoc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]
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2019-07-19 [SCH,PCB] Replace J4 with Phoenix connector
    Change C43 from 100pF to 100nF
    Remove C51 and add another cap next to C43 for VDDA
    Import changes to PCB (includes adding the TVS diodes from Hunter's commit)
    [Connectors-V.PcbLib, Connectors-V.SchLib, Connectors.SchLib, MCU B.SchDoc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]
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2019-07-21 [SCH] update parameters, fix XA1110 sch symbol, inconsistent reresistors R49 R52
    [Sensors.SchDoc]
2019-07-21 [LIB] fix XA1100 schematic symbol
    [Gas Monitor Components.SchLib]
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2019-07-24 Resolve DRC errors, replace IFA with SMA, organize designators
    [Amplifiers.SchDoc, Connectors.SchLib, Gas Monitor Components.SchLib, Gas Monitor.PrjPcb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]
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2019-07-24 Check impedance matching, add stitching, tent vias, fix silk clearances
    [Gas Monitor.PrjPcb]
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2019-07-29 [SCH,LIB] Update capacitor values
    Went through each schematic EXCEPT Sensors.SchDoc, checked each capacitor to see if they have a part number. Since the PCB has already been ordered with most passives having been changed to 0402, che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
    I then replaced all capacitors in the schematics with the new appropriate part and retained their designator value.
    [Amplifiers.SchDoc, Capacitors.SchLib, Gas Monitor.PrjPcb, Inductors.SchLib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]
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2019-07-30 fix parameters, generate first complete BOM
    [Gas Monitor Rev B - BOM -- RELEASE 2019-07-30.xls, MCU A.SchDoc, Sensors.SchDoc, USB-UART.SchDoc]
2019-07-30 fix BOM errors (parameters), generate new RELEASE BOM
    [Gas Monitor Rev B - BOM -- RELEASE 2019-07-30.xls, Power Supply.SchDoc, Sensors.SchDoc, USB-UART.SchDoc]
2019-07-30 [SCH] Fix some more PNs to be CT instead of DR
    [Power Supply.SchDoc, Sensors.SchDoc, VAMoS RevB 0730 1000AM BOM.xls]
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2019-08-05 Replace MCU with ESP32-WROOM-32U module, change USB-UART,remove flash, change SD signalling to SPI
    [Gas Monitor Components.PcbLib, Gas Monitor.PrjPcb, MCU A ESP32-WROOM-32U.SchDoc, Sensors.SchDoc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]
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2019-08-06 Add 12V_ALPHS power LED, add pullup for temp sense, change LED power to 5V, RGB pinout fix, add hardware TODO .txt
    [MCU A ESP32-WROOM-32U.SchDoc, Power Supply.SchDoc, Sensors.SchDoc]
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2019-08-07 Swap CP2104 for CP2102, add bootstrapping info, TPs on bootstrap pins, boot button, reset pullup
    To match the ESP32 DevKitC reference design (our new development board): https://www.espressif.com/sites/default/files/documentation/esp32-devkitc-v4_reference_design.zip
    [Connectors-V.PcbLib, Gas Monitor.PrjPcb, ICs-V.PcbLib, ICs-V.SchLib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]
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2019-08-09 remove silkscreen from pads in FPs, resolve all DRC errors
    [Gas Monitor Components.PcbLib, Gas Monitor.PrjPcb, ICs-V.PcbLib, Power Supply.SchDoc]
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2019-08-10 Add useful silkscreen labels, TPs to SENSOR_VN & -VP ...
    Thicker traces, larger vias, stitching vias, 50 Ohm impedence matching on GPS antenna, board edge clearance to 20mil, add power planes to 12V and 6V5
    [Gas Monitor.PrjPcb, MCU A ESP32-WROOM-32U.SchDoc]
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2019-08-22 Replace LM660 with LM664 with same SOIC-14 footprint, lower power rail to 3V3, rename ALPHS from 0-7 to 1-8 to match sensor input
    [Amplifiers.SchDoc]
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2019-08-23 Fix SD signal lines - MOSI and CS
    [Microcontroller.SchDoc]
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2019-08-25 Fix SD card lines - MISO and CLK needed to be shifted up one
    [Microcontroller.SchDoc]
2019-08-25 Revert SD card changes - correct for MICRO-SD
    [Microcontroller.SchDoc]
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
